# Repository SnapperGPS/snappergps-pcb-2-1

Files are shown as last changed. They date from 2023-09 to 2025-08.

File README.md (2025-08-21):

# snappergps-pcb-2-1

This is an alternative version of the original SnapperGPS receiver.
Just like [V1.0.0](https://github.com/SnapperGPS/snappergps-pcb), [V2.0.0](https://github.com/SnapperGPS/snappergps-pcb-2), and [V2.2.0](https://github.com/SnapperGPS/snappergps-pcb-2-2), it is a small, low-cost, and low-power GNSS receiver intended for non-real-time wildlife tracking.
It employs the snapshot GNSS technology, which offloads the computational expensive data processing to the cloud, and:

* Measures 27.3 mm x 36.4 mm,

* Operates for more than a year on two button batteries,

* Weighs 9.5 g or 13.0 g (depending on the type of batteries),

* Has enough memory to provide about 22,000 position fixes,

* Captures fixes in user-defined time intervals or externally triggered,

* Needs only 12 ms of signal reception for a fix,

* Employs multiple satellite systems for high reliability (GPS, Galileo, and BeiDou),

* Achieves a median real-world tracking accuracy of about 15 m (before smoothing),

* Maintains a real-time clock to accurately timestamp the fixes,

* Measures the temperature in addition, and

* Is configured via USB in your browser without the need to install a driver or an app.

This repository contains the hardware design files that can be used to replicate a SnapperGPS receiver V2.1.0.

If you use SnapperGPS hardware or software for research, please consider citing our publications.

For the hardware:

> Jonas Beuchert, Amanda Matthes, and Alex Rogers. 2023. SnapperGPS: Open Hardware for Energy-Efficient, Low-Cost Wildlife Location Tracking with Snapshot GNSS. Journal of Open Hardware, 7(1): 2, pp. 1–13. [https://doi.org/10.5334/joh.48](https://openhardware.metajnl.com/articles/10.5334/joh.48/).

For the cloud-processing software:

> Jonas Beuchert and Alex Rogers. 2021. SnapperGPS: Algorithms for Energy-Efficient Low-Cost Location Estimation Using GNSS Signal Snapshots. In SenSys ’21: ACM Conference on Embedded Networked Sensor Systems, November, 2021, Coimbra, Portugal. ACM, New York, NY, USA, 13 pages. https://doi.org/10.1145/3485730.3485931.

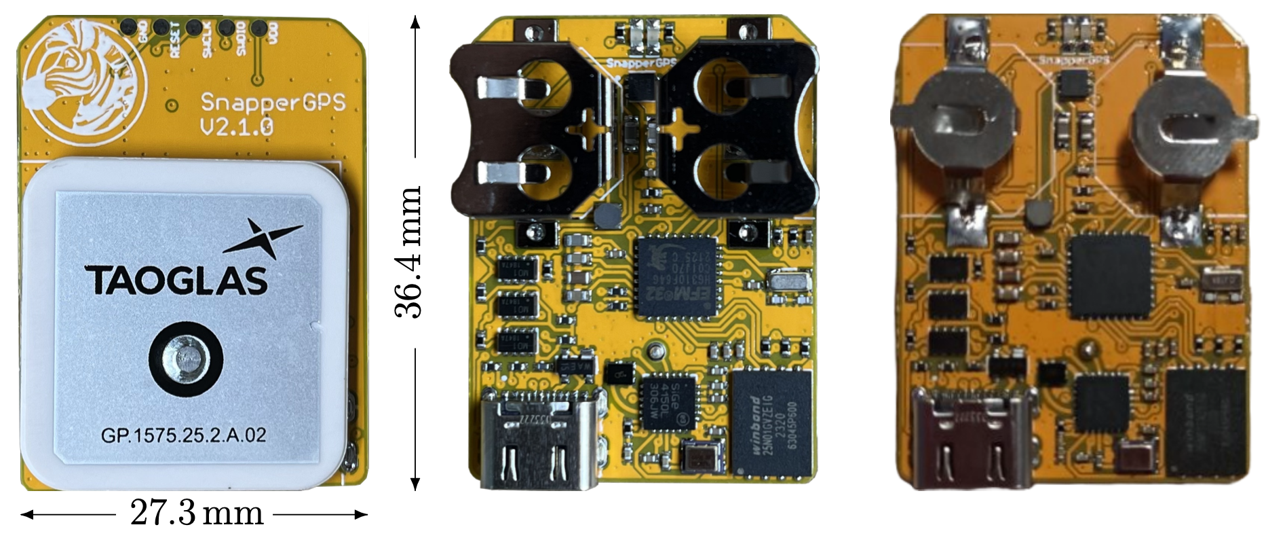
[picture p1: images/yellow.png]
SnapperGPS PCB
|  | 
|:--:| 
| *Figure 1: Top view (left) and bottom views (centre, right) of assembled SnapperGPS receivers V2.1.0 with a passive ceramic patch antenna and holders for two LR44 or SR44 button cells (centre) or two LR41 or SR41 button cells (right). This version is similar to V2.0.0, but does not come with GPIOs or a connector for an external antenna.* |

**Table of Contents**

1. [Changes from previous versions](#changes-from-previous-versions)

2. [Workflow](#workflow)

3. [Getting started](#getting-started)

4. [Repository Structure](#repository-structure)

5. [Professional Manufacturing](#professional-manufacturing)

6. [Hand Assembly](#hand-assembly)

7. [Testing](#testing)

8. [Hardware Overview](#hardware-overview)

9. [Pinout](#pinout)

10. [Bill of Materials](#bill-of-materials)

11. [Additional Resources](#additional-resources)

## Changes from previous versions

The main changes from V1.0.0 are:

* The antenna is integrated into the PCB. No external active antenna is used anymore.

* The receiver is powered by two LR44, SR44, LR41, or SR41 batteries rather than a lithium-ion polymer (LiPo) battery. These are easier to obtain, cheaper, and simpler to ship, but also a bit heavier and prevent the use of custom battery sizes.

* The board is a bit larger with 27.3 mm x 36.4 mm, although, this now includes the antenna and battery footprints.

* The memory is large enough to collect data for 22,000 fixes. Initially, V1.0.0 only supported a smaller memory for 11,000 fixes, although, it can now be upgraded to the larger memory version, too.

* The board (including antenna and batteries) weighs at least around 9.5 g. Depending on the choice of antenna and battery, this can be heavier or lighter than V1.0.0.

* The energy consumption is a little lower with 1 μA sleeping current @ 3 V rather than 1-2 μA  sleeping current @ 3.7 V. However, you should not feel the difference in practice.

The main changes from V2.0.0 are:

* An optional external active antenna cannot be used anymore.

* No general-purpose input/output (GPIO) pins are exposed. Therefore, no daughter-board can be connected.

* The board is a bit smaller with 27.3 mm x 36.4 mm.

* The board (including antenna and batteries) can weigh as little as 9.5 g. This is a bit lighter than V2.0.0.

* The board does not have an option to use a thicker 4 mm antenna, just a thinner 2 mm antenna. This reduces signal quality in contrast to V2.0.0 with the 4 mm antenna.

To summarise, V2.1.0 is a little smaller and lighter than V2.0.0 and should probably be the preferred version for deployments where size and weight are crucial.
However, for deployments with less restrictive weight/size constraints, V2.0.0 with the 4 mm antenna should probably be preferred to improve signal quality.
In addition, V2.0.0 is required if a daughter-board shall be connected.

## Workflow

- Get/build your SnapperGPS receiver (see sections below).
- [Configure](https://snappergps.info/configure) your SnapperGPS receiver in your browser for your deployment.
- Deploy your SnapperGPS receiver.
- The SnapperGPS receiver captures GNSS snapshots according to your configuration.
- Recover your SnapperGPS receiver.
- [Upload](https://snappergps.info/upload) the data from your SnapperGPS receiver to our server.
- [Download](https://snappergps.info/view) the track of your surveilled animal.

## Getting started

You already have a SnapperGPS receiver?
See [here](GETTING-STARTED.md) how to get started.
The instructions are for V1.0.0, but V2.1.0 works very similar.

You need to build a receiver first? Keep reading.

## Repository Structure

The two files `.brd` and `.sch` are CAD files that contain the PCB's board design and schematic, respectively. They have been created with Autodesk EAGLE 9.6.2, but should be compatible with other electronic design software.

The directory `CAMOutputs` includes the Gerber files and drill file, which are necessary for PCB manufacturing.

The two files `.mnb` and `.mnt` can be used for a pick-and-place machine and describe the component positions and orientations on the bottom and top layer, respectively.

## Professional Manufacturing

The simplest way to replicate SnapperGPS is to upload the BOM, the Gerber files, the drill file, and the pick and place files to an online PCB manufacturing and assembly service. They will source the components, print the PCB, and assemble the board.

We recommend a thickness between 0.8 and 1.6 mm for the four-layered board. The thinner, the lighter.
The substrate can be FR-4 and hot air solder leveling (HASL) or electroless nickel immersion gold (ENIG) can be used for the finish.

You can find an FAQ on prefessional manufacturing in [the discussions forum](https://github.com/orgs/SnapperGPS/discussions/22).

## Hand Assembly

An alternative to prefessional manufacturing is to just obtain the SnapperGPS PCB from a PCB manufacturer and to manually assembly the board.
Hand-soldering a board takes less than 2 h for a skilled person, but requires intermediate equipment and skills and potentially additional time for testing, debugging, and re-work.

You can find instructions [here](https://github.com/SnapperGPS/snappergps-pcb/blob/main/README.md#hand-assembly).

## Testing

Some basic testing:

* Open [the SnapperGPS web app](https://snappergps.info) in Microsoft Edge or Google Chrome or download it from [the Microsoft Store](https://apps.microsoft.com/store/detail/snappergps/9P9RPRS6LSMM) or [Google Play](https://play.google.com/store/apps/details?id=com.herokuapp.snapper_gps.twa). (Alternatively, you can also host the SnapperGPS web app yourself, as described in [the _snappergps-app_ repository](https://github.com/SnapperGPS/snappergps-app)).

* Go to the *Configure* page and click/tap on *Pair receiver*.

* The connected SnapperGPS receiver should now be selectable in a pop-up window.

* After pairing, confirm that the receiver information in the table on the top of the page is appropriate, including on-board time and firmware version. The snapshot count should be zero.

* Check the measured battery voltage in the table at the top of the *Configure* page. We recommend around 3 V before a long-term deployment.

* Select some configuration parameters in the app and click/tap on *Configure*.

* Disconnect the SnapperGPS receiver.

* Record a few snapshots outdoors.

* Reconnect the SnapperGPS receiver.

* Go to the *Upload* page and follow the instructions to upload the snapshots from the SnapperGPS receiver to the server. Please select only snapshots for processing that you collected outdoors.

* Once processing is complete, inspect the calculated track on the *Download* page. There are also links to some of our tracks for comparison.

Testing the localisation accuracy:

* Record some data outdoors at a location with known coordinates.

* Upload it via the SnapperGPS app.

* Calculate the horizontal error between the estimated locations and the ground truth.

* We obtained median errors of 10-12 m, depending on the scenario.

Measuring the power consumption:

* Configure a SnapperGPS receiver using the SnapperGPS app.

* Power the SnapperGPS receiver from an external DC source with 3 V.

* Place an ammeter in series with the source.

* The current should be around 1 μA if the board is sleeping and the maximum current should be around 25 mA when capturing a snapshot. The charge consumption for a single snapshot should be <0.3 μAh.

Testing the flash memory:

* Record the maximum of 21824 snapshots.

* Transfer them to a host computer using the *Transfer data* button on the *Upload* page of the SnapperGPS web app.

* Ensure that all 21824 snapshots have been transferred and are provided as download.

## Hardware Overview

Please have a look at our [paper](https://doi.org/10.5334/joh.48).

## Pinout

We expose the VDD, GND, RESET, SWCLK, and SWDIO pins of the MCU on the the PCB.
The last two allow for debugging or flashing using [Serial Wire Debug (SWD)](https://community.silabs.com/s/article/serial-wire-debug-swd-x).
All five circular pads have a spacing of 0.1 in and, hence, the same as common PCB headers.

All five pads are labelled on the silkscreen of the PCB.

```
┌───────────────────────────────┐
│   ○     ○     ○     ○     ○   │
│  GND  RESET SWCLK SWDIO  VDD  │
│                               │
```

## Bill of Materials

The table below lists the electronic components that are needed to assemble a single SnapperGPS board.
For one component, you have got two options each to create different SnapperGPS versions based on an identical PCB:
* J4, J5: These are the battery holders. Use the Keystone Electronics 2996 or 2996TR for LR44 and SR44 button batteries (Figure 1, centre), which are easy to source. Use Hong Kong CCD 704833 or similar for LR41 and SR41 button batteries (Figure 1, right). These are a bit harder to source, but using them saves about 3.5 g in total.

|Designator                                    |Qty|Manufacturer                  |Part #                                 |Description/Value                                            |Package/Footprint|Mounting Type|Notes                                                                          |Supplier URL                                                                                           |
|----------------------------------------------|--:|------------------------------|---------------------------------------|-------------------------------------------------------------|-----------------|-------------|-------------------------------------------------------------------------------|-------------------------------------------------------------------------------------------------------|
|C4, C8, C10, C12, C13, C14, C16, C17, C20, C23| 10|Murata                        |GRM155R60J104KA01D                     |Ceramic capacitor, 100 nF                                    |0402             |SMD          |                                                                               |https://www.digikey.com/en/products/detail/murata-electronics/GRM155R60J104KA01D/490-6287-1-ND/3845484 |
|C3, C5, C6, C7, C9                            |  5|Murata                        |GRM155R60J103KA01D                     |Ceramic capacitor, 10 nF                                     |0402             |SMD          |                                                                               |https://www.digikey.com/en/products/detail/murata-electronics/GRM155R60J103KA01D/490-6286-1-ND/3845483 |
|C21, C22                                      |  2|Murata                        |GRM1555C1H180JA01D                     |Ceramic capacitor, 18 pF                                     |0402             |SMD          |                                                                               |https://www.digikey.com/en/products/detail/murata-electronics/GRM1555C1H180JA01D/2854383               |
|C11, C19                                      |  2|Murata                        |GRM188R60J105KA01D                     |Multi-layer ceramic capacitor, 1 uF, 6.3 V, X5R              |0603             |SMD          |                                                                               |https://www.digikey.com/en/products/detail/murata-electronics/GRM188R60J105KA01D/490-1550-1-ND/587755  |
|C18                                           |  1|Murata                        |GRM185R60J475ME15D                     |Multi-layer ceramic capacitor, 4.7 uF, 6.3 V, X5R            |0603             |SMD          |                                                                               |https://www.digikey.com/en/products/detail/murata-electronics/GRM185R60J475ME15D/490-3892-1-ND/965934  |
|C15, C26                                      |  2|Murata                        |GRM188R60J106KE47D                     |Multi-layer ceramic capacitor, 10 uF, 6.3 V, X5R             |0603             |SMD          |                                                                               |https://www.digikey.com/en/products/detail/murata-electronics/GRM188R60J106KE47D/490-12538-1-ND/5797528|
|C27                                           |  1|Murata                        |GRM188R60G226MEA0D                     |Multi-layer ceramic capacitor, 22 uF, 6.3 V, X5R             |0603             |SMD          |                                                                               |https://www.digikey.com/en/products/detail/murata-electronics/GRM188R60G226MEA0D/2334877               |
|L2                                            |  1|Murata                        |BLM15HB221SH1D                         |Ferrite bead                                                 |0402             |SMD          |                                                                               |https://www.digikey.com/en/products/detail/murata-electronics/BLM15HB221SH1D/6798444                   |
|R11, R12                                      |  2|Yageo                         |RC0402FR-0715RL                        |Resistor, 15R                                                |0402             |SMD          |                                                                               |https://www.digikey.com/en/products/detail/yageo/RC0402FR-0715RL/311-15LRCT-ND/2827914                 |
|R15, R16                                      |  2|Yageo                         |RC0402FR-071KL                         |Resistor, 1K                                                 |0402             |SMD          |                                                                               |https://www.digikey.com/en/products/detail/yageo/RC0402FR-071KL/726513                                 |
|R10, R13, R17                                 |  3|Yageo                         |RC0402FR-074K7L                        |Resistor, 4K7                                                |0402             |SMD          |                                                                               |https://www.digikey.com/en/products/detail/yageo/RC0402FR-074K7L/311-4-7KLRCT-ND/2827881               |
|R7, R8                                        |  2|Yageo                         |RC0402FR-075K1L                        |Resistor, 5K1                                                |0402             |SMD          |                                                                               |https://www.digikey.com/en/products/detail/yageo/RC0402FR-075K1L/726624                                |
|R18                                           |  1|Yageo                         |RC0402FR-076K8L                        |Resistor, 6K8                                                |0402             |SMD          |                                                                               |https://www.digikey.com/en/products/detail/yageo/RC0402FR-076K8L/311-6-80KLRCT-ND/729589               |
|R14, R19                                      |  2|Yageo                         |RC0402FR-0710KL                        |Resistor, 10K                                                |0402             |SMD          |                                                                               |https://www.digikey.com/en/products/detail/yageo/RC0402FR-0710KL/726523                                |
|R1, R2, R3, R4, R5, R6, R9                    |  7|Yageo                         |RC0402FR-07100KL                       |Resistor, 100K                                               |0402             |SMD          |                                                                               |https://www.digikey.com/en/products/detail/yageo/RC0402FR-07100KL/311-100KLRCT-ND/729473               |
|Q2                                            |  1|Jauch Quartz                  |Q 0,032768-JTX310-12,5-10-T1-HMR-50K-LF|Crystal, 32.768 kHz ±10 ppm, 12.5 pF, 50 kOhm                |2-SMD            |SMD          |Possible substitute: Epsom, X1A0001410004 FC-135R 32.768KHZ 9PF                |https://www.digikey.com/en/products/detail/jauch-quartz/Q-0-032768-JTX310-12-5-10-T1-HMR-50K-LF/8108077|
|D1                                            |  1|Rohm Semiconductor            |SML-D12M1WT86                          |LED, yellow-green, 572 nm, 2.2 V                             |0603             |SMD          |                                                                               |https://www.digikey.com/en/products/detail/rohm-semiconductor/SML-D12M1WT86/SML-D12M1WT86CT-ND/5843861 |
|D2                                            |  1|Rohm Semiconductor            |SML-D12U1WT86                          |LED, red, 620 nm, 2.2 V                                      |0603             |SMD          |                                                                               |https://www.digikey.com/en/products/detail/rohm-semiconductor/SML-D12U1WT86/SML-D12U1WT86CT-ND/5843858 |
|TCXO1                                         |  1|Connor Winfield               |D32G-016.368M                          |Temperature compensated oscillator, 16.384 MHz               |3.2x2.5          |SMD          |Possible substitutes: EPSON, X1G005441030112 or TXC Corporation, 7Q-16.368MBG-T|https://www.digikey.com/en/products/detail/connor-winfield/D32G-016-368M/3641696                       |
|U2                                            |  1|Skyworks Solutions Inc.       |SE4150L-R                              |RF receiver                                                  |24-QFN           |SMD          |                                                                               |https://octopart.com/se4150l-r-skyworks+solutions-20439429                                             |
|SAW1                                          |  1|Abracon LLC                   |AFS20A42-1575.42-T3                    |SAW filter, 1.575 GHz, BW 42 MHz                             |4-SMD            |SMD          |Possible substitute: AFS20A02-1575.42-T3                                       |https://www.digikey.com/en/products/detail/abracon-llc/AFS20A42-1575-42-T3/535-12069-1-ND/4075659      |
|U1                                            |  1|Silicon Labs                  |EFM32HG310F64G-C-QFN32R                |Microcontroller                                              |32-QFN           |SMD          |Possible substitutes: EFM32HG310F64G-A-QFN32R or EFM32HG310F64G-B-QFN32R       |https://www.digikey.com/en/products/detail/silicon-labs/EFM32HG310F64G-C-QFN32R/336-6165-1-ND/10314104 |
|U3                                            |  1|Nexperia                      |PRTR5V0U2AX,235                        |TVS diode, 5.5 V                                             |SOT143B          |SMD          |                                                                               |https://www.digikey.com/en/products/detail/nexperia-usa-inc/PRTR5V0U2AX235/1727-5862-1-ND/2698064      |
|IC1                                           |  1|Winbond Electronics           |W25N01GVZEIG                           |NAND flash, 1 GBit                                           |WSON-8           |SMD          |Possible substitute:  W25N512GVEIG (512 MBit)                                  |https://www.digikey.com/en/products/detail/winbond-electronics/W25N01GVZEIG-TR/5803931                 |
|Q1, Q3, Q4                                    |  3|Rohm Semiconductor            |TT8M1TR                                |Mosfet array N and P-channel, 20 V, 2.5 A, 1 W               |8-SMD            |SMD          |                                                                               |https://www.digikey.com/en/products/detail/rohm-semiconductor/TT8M1TR/5042837                          |
|J1                                            |  1|JAE Electronics               |DX07S016JA1R1500                       |USB-C receptacle connector, 24 Pins (16+8 dummy), right angle|                 |through-hole |                                                                               |https://www.digikey.com/en/products/detail/jae-electronics/DX07S016JA1R1500/11585731                   |
|ANT1                                          |  1|Taoglas                       |GP.1575.25.2.A.02                      |GPS/GALILEO patch antenna                                    |25x25            |through-hole |                                                                               |https://www.digikey.com/en/products/detail/taoglas-limited/GP-1575-25-2-A-02/2332643                   |
|U6                                            |  1|Texas Instruments             |TPS61291DRVT                           |Boost Switching Regulator IC                                 |6-WSON           |SMD          |                                                                               |https://www.digikey.com/en/products/detail/texas-instruments/TPS61291DRVT/5012070                      |
|U7                                            |  1|Taiyo Yuden                   |MDMK2020T3R3MM                         |Fixed inductor, 3.3 uH, 1.15 A, 178 MOhm                     |2x2              |SMD          |                                                                               |https://www.digikey.com/en/products/detail/taiyo-yuden/MDMK2020T3R3MM/3479456                          |
|J4, J5                                        |  2|Keystone Electronics *or* Hong Kong CCD|2996 *or* 704833              |Battery holder (LR44/SR44 *or* LR41/SR41)                    |                 |SMD          |Possible substitute: Keystone Electronics, 2996TR                              |https://www.digikey.com/en/products/detail/keystone-electronics/2996TR/2746493 *or* https://www.aliexpress.com/item/32742124807.html|
|                                              |   |                              |                                       |                                                             |                 |             |                                                                               |                                                                                                       |

The BOM differs slightly from the one for initial SnapperGPS test boards, which was cheaper.
For example, we used cheaper TCXOs, the X1G005441030112 manufactured by EPSON or the 7Q-16.368MBG-T from the TXC Corporation, which cost around $2 instead of the expensive D32G-016.368M that costs $7-$8.
We had to introduce this change because of the on-going global supply chain disruptions and recommend to revert to one of the initial choices for replications, if possible, to reduce the overall cost.

## Additional resources

## Acknowledgements

This SnapperGPS receiver version was developed and is maintained by
[Jonas Beuchert](https://users.ox.ac.uk/~kell5462/) under supervision of
[Alex Rogers](https://www.cs.ox.ac.uk/people/alex.rogers/)
in the Department of Computer Science
of the University of Oxford.

Jonas Beuchert is
funded by the EPSRC Centre for Doctoral Training in
Autonomous Intelligent Machines and Systems
(DFT00350-DF03.01) and develops
SnapperGPS as part of his doctoral studies.
The implementation of SnapperGPS 
was co-funded by EPSRC IAA Technology Funds
(D4D00010-BL14 and D4D00190-BL03.01).

##

This documentation is licensed under a
[Creative Commons Attribution 4.0 International License][cc-by].

[][cc-by]

[cc-by]: http://creativecommons.org/licenses/by/4.0/
[cc-by-image]: https://i.creativecommons.org/l/by/4.0/88x31.png

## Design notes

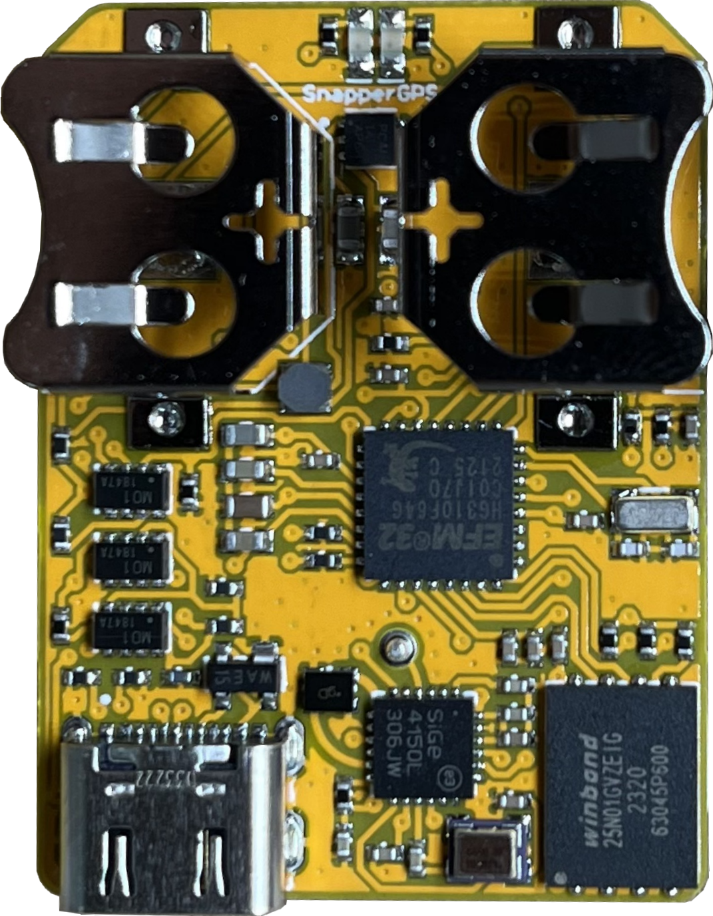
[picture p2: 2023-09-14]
images/yellow-bottom.png

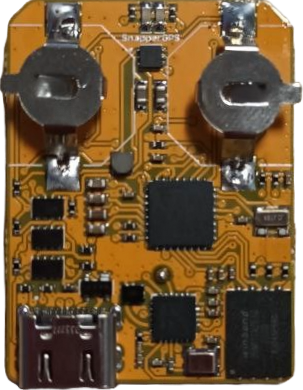
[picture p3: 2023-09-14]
images/yellow-bottom-lr41.png

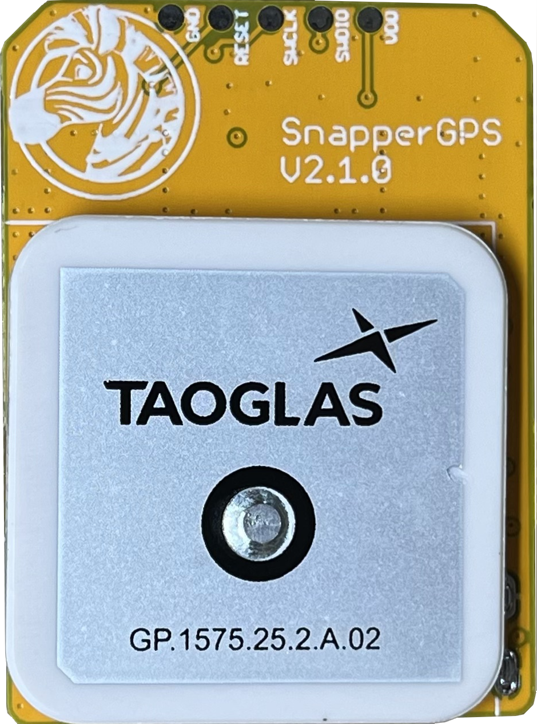
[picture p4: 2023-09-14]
images/yellow-top.png

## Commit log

2023-09-14 Rename design files
    [snappergps_board_2_1_0.brd, snappergps_board_2_1_0.sch]
2023-09-14 Add gerber and drill files
    [copper_bottom_l4.gbr, copper_inner_l2.gbr, copper_inner_l3.gbr, copper_top_l1.gbr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]
2023-09-14 Tweak schematic
    [snappergps_board_2_1_0.sch]

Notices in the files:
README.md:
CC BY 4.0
